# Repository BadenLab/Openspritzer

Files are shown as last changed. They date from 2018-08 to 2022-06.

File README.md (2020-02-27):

<p align="right">
<h1 align="center">Openspritzer</h1></p>
<h3 align="center">An open hardware pressure ejection system for reliably delivering picolitre volumes.</h3>
<p align="center"><h6 align="right">by C.J. Forman, H. Tomes, B. Mbobo, R.J. Burman, M. Jacobs, T Baden &
J.V. Raimondo</h6></p>
<p align="center"><h6 align="right">adapted by M.J.Y. Zimmermann</h6></p>
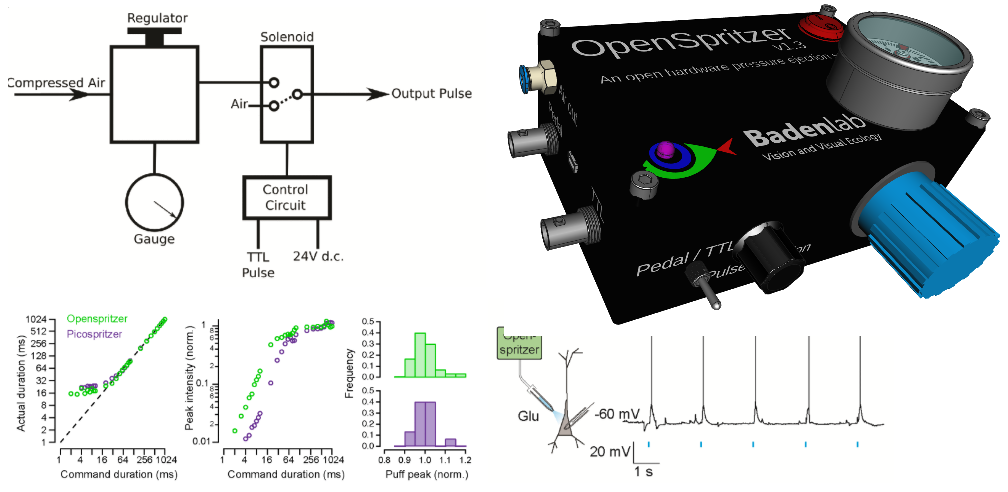
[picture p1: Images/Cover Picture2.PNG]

</p>

<p align="justify">Designed for ease of use, robustness and low-cost, the “Openspritzer” is an open hardware “Picospritzer” as routinely used
in biological labs around the world. The performance of Openspritzer and commercial alternatives is effectively indistiguishable.

<p align="justify">The system is based on a solenoid valve connected to a pressure gauge. Control can be attained directly via an external TTL pulse
or internally through an Arduino set by a rotary encoder. The basic setup can be put together for 3-400€, or substantially less if you
are prepare to shop around.

<p align="justify">We anticipate that due to its high performance and low cost Openspritzer will be of interest to a broad range of researchers working
in the life and physical sciences.</p>

This project is licensed under the [GNU General Public License v3.0](https://github.com/BadenLab/Openspritzer/blob/master/LICENSE)<br>
The hardware is licensed under the [CERN OHL v1.2](https://github.com/BadenLab/LED-Zappelin/blob/master/PCB/LICENSE)

***

- [A £350 DIY opensource microinjector](#Openspritzer,-a-DIY-opensource-microinjector.)
- [An efficient device that provides similar level of control as commercial systems](#Openspritzer-rivals-the-performance-of-commercial-systems.)
- [OpenSpritzer can deliver neurotransmitters with millisecond precision to control neural activity](#Openspritzer-in-neuroscience-experiments.)
- [OpenSpritzer is suitable for delivering infectious agents including viral delivery of opsins for optogenetics](#Openspritzer-for-microinjection-of-infectious-agents)

***

## Openspritzer, a DIY opensource microinjector.

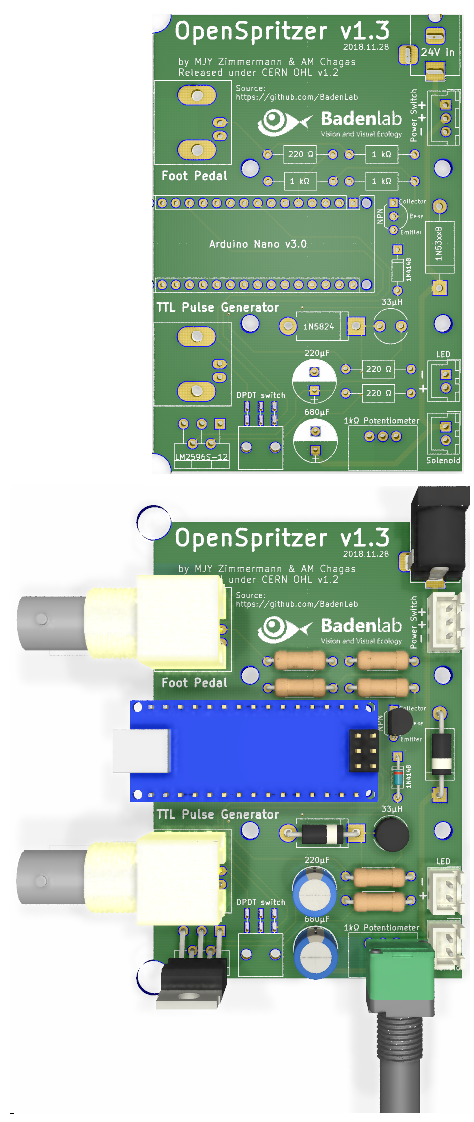
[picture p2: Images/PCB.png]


<p align="justify">Compared to similar commercial systems that can cost up to several thousand pounds, the cost of the fully equiped Openspritzer (~£350) makes it
particularly attractive for those wishing to pursue cutting-edge techniques in low ressource environments.</p>

This repository contains detailed [assembly instructions](https://github.com/BadenLab/Openspritzer/tree/master/Instruction%20Manual) and an operation manual for Openspritzer. The [bill of material](https://github.com/BadenLab/Openspritzer/blob/master/Bill%20of%20Materials/BOM.csv) details all pneumatic, mechanical and electronic components required along with possible supplier URL links.

To simplify the wiring assembly, we have designed a customed [circuit board](https://github.com/BadenLab/Openspritzer/tree/master/PCB). PCB prototype companies will only need the gerber.zip folder to be sent to them for production.

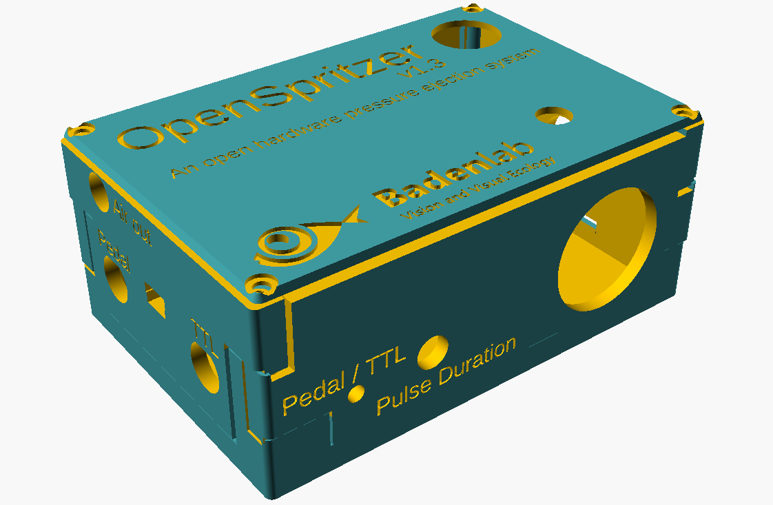
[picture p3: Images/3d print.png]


We used [OpenSCAD](http://openscad.org) to design [3D files](https://github.com/BadenLab/Openspritzer/tree/master/3D%20Designs) that could be printed to efficiently hold all openspritzer components.

The device is controled by an arduino nano. The [.ino code](https://github.com/BadenLab/Openspritzer/tree/master/Arduino%20Code) can be modified and uploaded as many times as you like. The way the Openspritzer code has been constructed allows simple modification of key parameters. These are all included at the beginning of the code for ease of reference.

***

## Openspritzer rivals the performance of commercial systems.

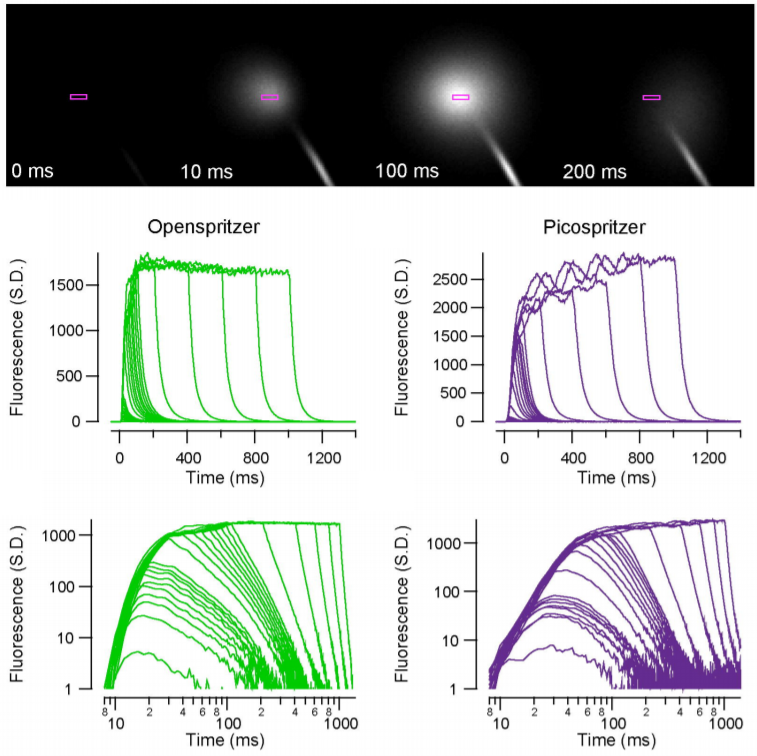
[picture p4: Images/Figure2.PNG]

Openspritzer control over dose delivery matches that of a leading commercial alternative.

<p align="justify">To directly assess the time precision and reliability of Openspritzer we visualised fluorescent dye puffs from a sharp microelectrode under two-photon microscopy. The images were taken from a puff with a duration of several seconds using a wide area scan (rectangles).

<p align="justify">Fluorescence profiles of different command-duration puffs are shown for Openspritzer (green) and Picospritzer, a popular microinjection system(purple), respectively. The same data is shown again in log-log space to highlight details of shorter pulses. Overall, both devices behave in a very similar way in terms of providing effective and near linear control over the total dosage.</p>

***

## Openspritzer in neuroscience experiments.

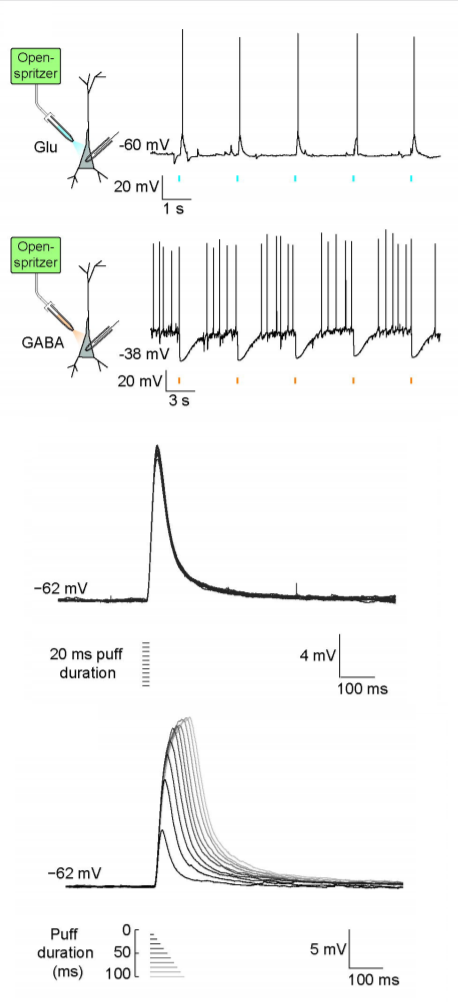
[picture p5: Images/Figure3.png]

Openspritzer controls neural activity by delivering neurotransmitters with millisecond precision.

<p align="justify">To demonstrate the utility of Openspritzer, we use it in a series of standard neurobiological applications:
We delivered precise amounts of glutamate(cyan) and GABA(orange) to hippocampal neurons to elicit time- and dose-precise excitatory and inhibitory responses respectively, while monitoring the voltage response of the recorded neuron in current-clamp mode.

<p align="justify">20 ms doses of glutamate (100 μM) reliably evoked excitatory postsynaptic potentials (EPSPs) and action potentials. Similarly, action potential activity elicited via somatic current injection could be suppressed by 20 ms puffs of GABA (100 μM).

<p align="justify">To assess the accuracy of the drug delivery, we applied 10 sweeps where a 20 ms glutamate puff was applied after 500 ms produced almost identical EPSPs demonstrating the precise timing of Openspritzer and highly conserved puff volumes.

<p align="justify">Then, to test the effect of command duration on effective dose delivey, we next applied puffs of increasing duration from 10 to 100 ms in 10 ms steps. Here, each additional 10 ms increase in duration produced a clear increase in both EPSP duration and amplitude. These results confirm the reliability and precision of Openspritzer for delivering small doses of an agent to a widely used biological sample in a controlled manner.</p>

***
***

<p align="justify">To demonstrate the utility of Openspritzer we performed multiple example experiments delivering agents ranging in size from single molecules to whole bacteria. Each experiment depended critically on the performance of the device. The spatio-temporal control of reagent delivery affored by Openspritzer is a primary feature of the device.

<p align="justify">Furthermore, with the emergence of a plethora of popular new techniques involving genetic manipulation of tissue and organisms, such as optogenetics and CRISPR, the demand for equipment with the functionality of Openspritzer is likely to increase.

<p align="justify">We anticipate that due to its high performance and low cost Openspritzer will be of interest to a broad range of researchers working in the life and physical sciences.</p>

<p align="center"><h6 align="right">Source: CJ. Forman et al, 2017 --  https://www.nature.com/articles/s41598-017-02301-2   </h6>

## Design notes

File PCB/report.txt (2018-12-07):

Plot file “C:\Users\Maxime\Documents\GitHub\Openspritzer\Printed Circuit Board\OpenSpritzer v1.2\gerber\OpenSpritzer_1.2-F.Cu.gbr” created.
Plot file “C:\Users\Maxime\Documents\GitHub\Openspritzer\Printed Circuit Board\OpenSpritzer v1.2\gerber\OpenSpritzer_1.2-B.Cu.gbr” created.
Plot file “C:\Users\Maxime\Documents\GitHub\Openspritzer\Printed Circuit Board\OpenSpritzer v1.2\gerber\OpenSpritzer_1.2-F.Adhes.gbr” created.
Plot file “C:\Users\Maxime\Documents\GitHub\Openspritzer\Printed Circuit Board\OpenSpritzer v1.2\gerber\OpenSpritzer_1.2-B.Adhes.gbr” created.
Plot file “C:\Users\Maxime\Documents\GitHub\Openspritzer\Printed Circuit Board\OpenSpritzer v1.2\gerber\OpenSpritzer_1.2-F.Paste.gbr” created.
Plot file “C:\Users\Maxime\Documents\GitHub\Openspritzer\Printed Circuit Board\OpenSpritzer v1.2\gerber\OpenSpritzer_1.2-B.Paste.gbr” created.
Plot file “C:\Users\Maxime\Documents\GitHub\Openspritzer\Printed Circuit Board\OpenSpritzer v1.2\gerber\OpenSpritzer_1.2-F.SilkS.gbr” created.
Plot file “C:\Users\Maxime\Documents\GitHub\Openspritzer\Printed Circuit Board\OpenSpritzer v1.2\gerber\OpenSpritzer_1.2-B.SilkS.gbr” created.
Plot file “C:\Users\Maxime\Documents\GitHub\Openspritzer\Printed Circuit Board\OpenSpritzer v1.2\gerber\OpenSpritzer_1.2-F.Mask.gbr” created.
Plot file “C:\Users\Maxime\Documents\GitHub\Openspritzer\Printed Circuit Board\OpenSpritzer v1.2\gerber\OpenSpritzer_1.2-B.Mask.gbr” created.
Plot file “C:\Users\Maxime\Documents\GitHub\Openspritzer\Printed Circuit Board\OpenSpritzer v1.2\gerber\OpenSpritzer_1.2-Dwgs.User.gbr” created.
Plot file “C:\Users\Maxime\Documents\GitHub\Openspritzer\Printed Circuit Board\OpenSpritzer v1.2\gerber\OpenSpritzer_1.2-Cmts.User.gbr” created.
Plot file “C:\Users\Maxime\Documents\GitHub\Openspritzer\Printed Circuit Board\OpenSpritzer v1.2\gerber\OpenSpritzer_1.2-Eco1.User.gbr” created.
Plot file “C:\Users\Maxime\Documents\GitHub\Openspritzer\Printed Circuit Board\OpenSpritzer v1.2\gerber\OpenSpritzer_1.2-Eco2.User.gbr” created.
Plot file “C:\Users\Maxime\Documents\GitHub\Openspritzer\Printed Circuit Board\OpenSpritzer v1.2\gerber\OpenSpritzer_1.2-Edge.Cuts.gbr” created.
Plot file “C:\Users\Maxime\Documents\GitHub\Openspritzer\Printed Circuit Board\OpenSpritzer v1.2\gerber\OpenSpritzer_1.2-Margin.gbr” created.
Plot file “C:\Users\Maxime\Documents\GitHub\Openspritzer\Printed Circuit Board\OpenSpritzer v1.2\gerber\OpenSpritzer_1.2-F.CrtYd.gbr” created.
Plot file “C:\Users\Maxime\Documents\GitHub\Openspritzer\Printed Circuit Board\OpenSpritzer v1.2\gerber\OpenSpritzer_1.2-B.CrtYd.gbr” created.
Plot file “C:\Users\Maxime\Documents\GitHub\Openspritzer\Printed Circuit Board\OpenSpritzer v1.2\gerber\OpenSpritzer_1.2-F.Fab.gbr” created.
Plot file “C:\Users\Maxime\Documents\GitHub\Openspritzer\Printed Circuit Board\OpenSpritzer v1.2\gerber\OpenSpritzer_1.2-B.Fab.gbr” created.
Plot file “C:\Users\Maxime\Documents\GitHub\Openspritzer\Printed Circuit Board\OpenSpritzer v1.2\gerber\OpenSpritzer_1.2-F.Cu.gbr” created.
Plot file “C:\Users\Maxime\Documents\GitHub\Openspritzer\Printed Circuit Board\OpenSpritzer v1.2\gerber\OpenSpritzer_1.2-B.Cu.gbr” created.
Plot file “C:\Users\Maxime\Documents\GitHub\Openspritzer\Printed Circuit Board\OpenSpritzer v1.2\gerber\OpenSpritzer_1.2-F.Adhes.gbr” created.
Plot file “C:\Users\Maxime\Documents\GitHub\Openspritzer\Printed Circuit Board\OpenSpritzer v1.2\gerber\OpenSpritzer_1.2-B.Adhes.gbr” created.
Plot file “C:\Users\Maxime\Documents\GitHub\Openspritzer\Printed Circuit Board\OpenSpritzer v1.2\gerber\OpenSpritzer_1.2-F.Paste.gbr” created.
Plot file “C:\Users\Maxime\Documents\GitHub\Openspritzer\Printed Circuit Board\OpenSpritzer v1.2\gerber\OpenSpritzer_1.2-B.Paste.gbr” created.
Plot file “C:\Users\Maxime\Documents\GitHub\Openspritzer\Printed Circuit Board\OpenSpritzer v1.2\gerber\OpenSpritzer_1.2-F.SilkS.gbr” created.
Plot file “C:\Users\Maxime\Documents\GitHub\Openspritzer\Printed Circuit Board\OpenSpritzer v1.2\gerber\OpenSpritzer_1.2-B.SilkS.gbr” created.
Plot file “C:\Users\Maxime\Documents\GitHub\Openspritzer\Printed Circuit Board\OpenSpritzer v1.2\gerber\OpenSpritzer_1.2-F.Mask.gbr” created.
Plot file “C:\Users\Maxime\Documents\GitHub\Openspritzer\Printed Circuit Board\OpenSpritzer v1.2\gerber\OpenSpritzer_1.2-B.Mask.gbr” created.
Plot file “C:\Users\Maxime\Documents\GitHub\Openspritzer\Printed Circuit Board\OpenSpritzer v1.2\gerber\OpenSpritzer_1.2-Dwgs.User.gbr” created.
Plot file “C:\Users\Maxime\Documents\GitHub\Openspritzer\Printed Circuit Board\OpenSpritzer v1.2\gerber\OpenSpritzer_1.2-Cmts.User.gbr” created.
Plot file “C:\Users\Maxime\Documents\GitHub\Openspritzer\Printed Circuit Board\OpenSpritzer v1.2\gerber\OpenSpritzer_1.2-Eco1.User.gbr” created.
Plot file “C:\Users\Maxime\Documents\GitHub\Openspritzer\Printed Circuit Board\OpenSpritzer v1.2\gerber\OpenSpritzer_1.2-Eco2.User.gbr” created.
Plot file “C:\Users\Maxime\Documents\GitHub\Openspritzer\Printed Circuit Board\OpenSpritzer v1.2\gerber\OpenSpritzer_1.2-Edge.Cuts.gbr” created.
Plot file “C:\Users\Maxime\Documents\GitHub\Openspritzer\Printed Circuit Board\OpenSpritzer v1.2\gerber\OpenSpritzer_1.2-Margin.gbr” created.
Plot file “C:\Users\Maxime\Documents\GitHub\Openspritzer\Printed Circuit Board\OpenSpritzer v1.2\gerber\OpenSpritzer_1.2-F.CrtYd.gbr” created.
Plot file “C:\Users\Maxime\Documents\GitHub\Openspritzer\Printed Circuit Board\OpenSpritzer v1.2\gerber\OpenSpritzer_1.2-B.CrtYd.gbr” created.
Plot file “C:\Users\Maxime\Documents\GitHub\Openspritzer\Printed Circuit Board\OpenSpritzer v1.2\gerber\OpenSpritzer_1.2-F.Fab.gbr” created.
Plot file “C:\Users\Maxime\Documents\GitHub\Openspritzer\Printed Circuit Board\OpenSpritzer v1.2\gerber\OpenSpritzer_1.2-B.Fab.gbr” created.

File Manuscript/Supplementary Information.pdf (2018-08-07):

## Supplementary Material

## Openspritzer: an open hardware pressure ejection system for reliably delivering picolitre volumes

Forman, C.J.¹,4§
, Tomes, H.

2

, Mbobo, B.²

, Baden, T¹,3,4§

., Raimondo, J.V.²,4§

Affiliations:
1) School of Life Sciences, University of Sussex, United Kingdom
2) Division of Physiology, Department of Human Biology, Neuroscience Institute and Institute of Infectious Disease and Molecular Medicine, Faculty of Health Sciences, University of Cape Town, Cape Town, South Africa
3) Institute for Ophthalmic Research, University of Tuebingen, Germany
4) TReND in Africa gUG (www.TReNDinAfrica.org)

§Correspondence: C.F.: chrisforman@cantab.net, T.B.: t.baden@sussex.ac.uk, J.V.R.: joseph.raimondo@uct.ac.za

Command duration is correlated to dosage

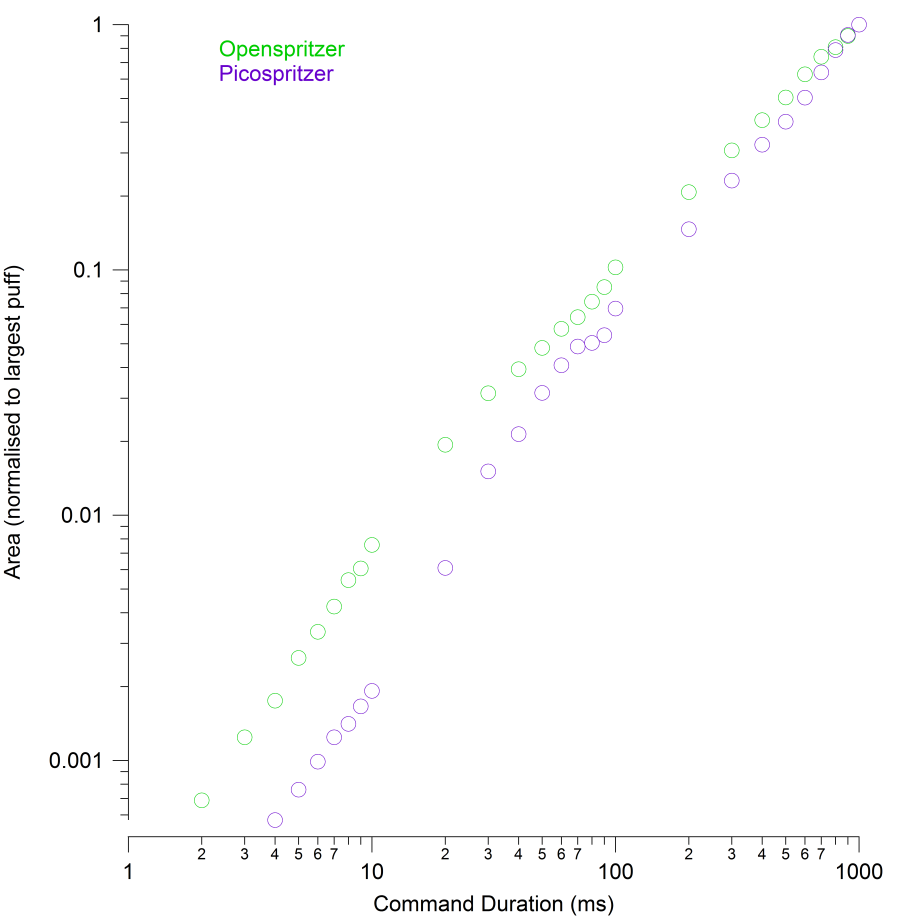
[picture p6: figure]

Supplementary Figure S1: The integrated area for each puff plotted against the command duration. The area under the puff profile is proportional to the dosage. Command duration and dosage are strongly correlated, regardless of the details of the puff profile over time.

Open Spritzer Construction

Overview

This document contains detailed assembly instructions and an operation manual for Openspritzer, and includes a parts list. The Arduino code and SCAD files for the exterior casing are provided and may be downloaded at http://raimondolab.com/Openspritzer/. The purpose of the device is to regulate the pressure and duration of a puff of compressed air. Typically the output port is connected to a glass puffer pipette which has been drawn into a sharp point with a narrow (<2-3 µm) diameter pore.
The device consists of a circuit board, a solenoid valve, a pressure regulator with a gauge and various interface components. Supplementary Fig. S2 shows the device without the covering lid and the solenoid displaced to expose the circuit board. The pressure regulator is mounted on the left and attached to the front panel via a retaining threaded ring that comes with the regulator. The circuit board is mounted onto attachment points on the floor of the box. It is situated next to the side wall containing the electronic interface components. There are two supports on which the solenoid can rest above the circuit board and an LED can be attached to a mount-point on the lid. There are also several retaining pillars which keep the solenoid in position. The lid has a block attached to it which acts to clamp the solenoid down when the box is closed.

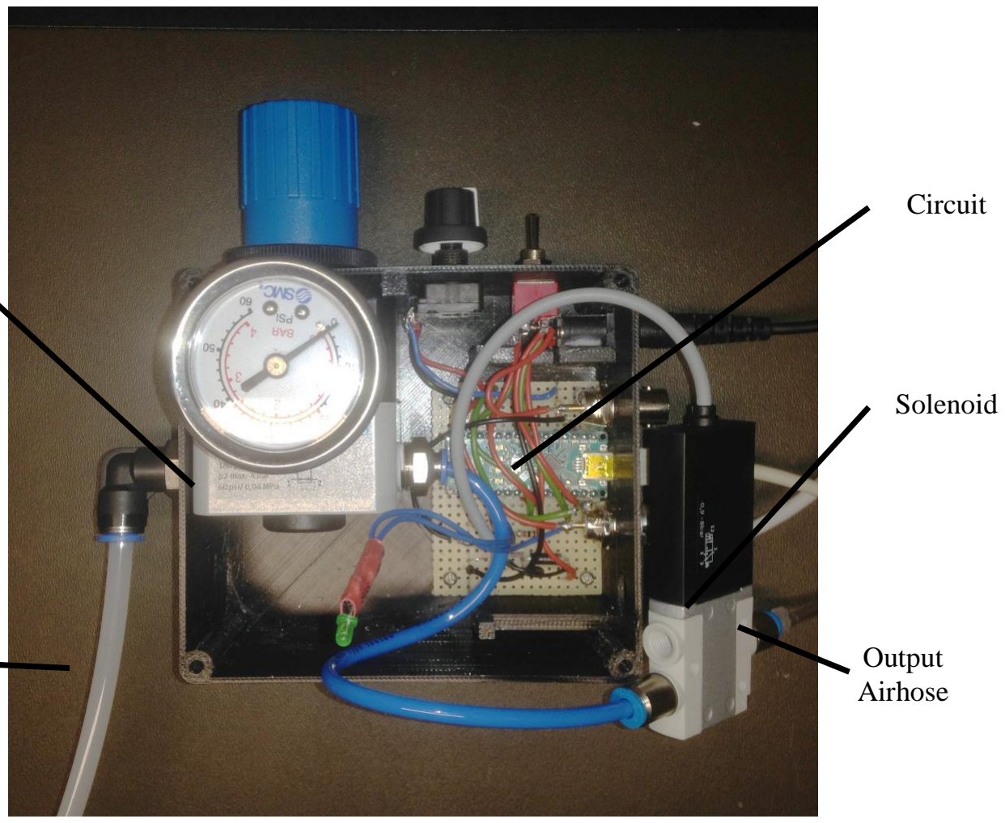
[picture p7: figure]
Solenoid; Circuit; Output Airhose

Supplementary Figure S2: Openspritzer consists of a pressure regulator, a solenoid and a control circuit. Its purpose is to control the strength and duration of a puff of compressed air, which is connected to a glass pipette that typically contains reagents for microinjection into biological samples.

Regulator
and Gauge

Input
Airhose

Parts List

Supplementary Table 1 has an exhaustive list of parts, suppliers and prices, allowing calculation of the total cost of parts, which is between £320 and £360 at submission, depending on how much of the full system one chooses to include. Much of the circuitry e.g. the Arduino, footswitch and toggle switch is purely for convenience. A core functional system consists of the regulator, solenoid and a much simpler control circuit under TTL pulse control. The simpler minimal circuit is indicated in the construction instructions below, and consists of the branch of the circuit containing the transistor.
In addition, prices are highly variable depending on local availability of components. For example the single most expensive component when we assembled ours was the regulator which cost £180 at the time. However, we subsequently found the same regulator for $43 in a different country. If one is prepared to shop around, we estimate that a functional Openspritzer without add-ons could be constructed for as little as £175. If one has all the components it takes approx 3 hours to construct a full Openspritzer depending on experience, and excluding the print time for the case and lid.
Frequently components only come in bags of 10 or 50 so if one only intends to fabricate a single device there may be an additional overhead of extra parts, depending on the flexibility of your supplier. For example ours cost £360 for the parts actually included in the device, but we paid £495 in total and now have some spare components for additional units.

4

Supporting Table S1 Parts schedule for Openspritzer

Part | Manufacturer | Manufacturers Number | Remarks | Quantity Essential

Component
Price

System
Price

Pack
| | | | | | | | price | Unit

Pneumatics
Solenoid (either 2 ms or 7 ms) | FESTO | MHE2-M1SH-3/2G-M7-K-RR | 2 ms response + cable | | 1 Yes | £80.00 | £80.00 | £80.00 | each
alternative | MHE2-M1H-3/2G-M7-K-RR | 7 ms response + cable
Precision pressure regulator | FESTO | LRP-1/4-4 | 0.05 to 4.0 bar | 1 Yes | £180.00 | £180.00 £180.00 each
Gauge | FESTO | MAP-40-4-1/8-EN | 0.0 to 4.0 bar, 1/8 inch thread
| alternative SMC | 4K84P | 0.0 to 4.0 bar, 1/8 inch thread | | 1 Yes | £30.00 | £30.00 | £30.00 | each
Push-in (6 mm) to thread (1/4") | FESTO | QSL-1/4-6 | 6 mm to 1/4 inch | | 1 Yes | £2.83 | £2.83 | £28.30 | Pack of ten
Push-in (4 mm) to thread (1/4") | FESTO | QS-1/4-4 | 4 mm to 1/4 inch | | 1 Yes | £1.76 | £1.76 | £17.60 | Pack of ten
Push-in (4 mm) to thread (M7) | FESTO | QSM-M7-4-I | 4 mm to M7 thread | | 2 Yes | £1.81 | £3.62 | £18.10 | Pack of ten
4mm OD plastic tubing | FESTO | PUN-4x0.75 | 4 mm OD and 10 bar | 12 cm | Yes | £0.09 | £0.09 | £35.50 | 50 m

Electronics
Arduino Nano | Arduino | | Arduino Nano | | 1 No | £4.00 | £4.00 | £4.00 | each
Darlington pair NPN transistor | Fairchild | KSP 13BU | Ic = 500 mA, Vces = 30 V | | 1 Yes | £0.12 | £0.12 | £1.20 | pack of ten
1 kΩ variable resistor | Vishay | 249BBHS0XB25102KA | panel mount | | 1 No | £7.53 | £7.53 | £7.53 | each
Knob for variable resistor | RS Online | 299-4957 | 6mm shaft radius | | 1 No | £0.17 | £0.17 | £0.85 | pack of five
DPDT switch | RS Online | 734-7016 | on-on panel mount | | 1 No | £1.13 | £1.13 | £5.65 | pack of five
SPST footswitch | RS Online | 335-319 | push-to-contact | | 1 No | £13.03 | £13.03 | £13.03 | each
24V dc desktop PSU 2.1 mm jack | RS Online | 436-058 | 24 V dc 1 A | | 1 Yes | £17.91 | £17.91 | £17.91 | each
2.1 mm right angle dc socket | RS Online | 884-0957 | 2.1 mm right angle | | 1 Yes | £0.93 | £0.93 | £4.65 | pack of five
Rect pin socket (through hole fem) | Digikey | SAM1222-01-ND | 1x1 | | 2 No | £0.81 | £1.62 | £1.62 | each
Rect pin socket (through hole fem) | Digikey | S7038-ND | 5x1 | | 1 No | £0.65 | £0.65 | £0.65 | each
Rect pin socket (through hole fem) | Digikey | 3M9514-ND | 3x1 | | 1 No | £0.64 | £0.64 | £0.64 | each
24 V Zener Diode | ON
Semiconductor 1N5359BG | 24 V | 1 Yes | £2.30 | £2.30 | £2.30 | each
1N4148 signal diode | Fairchild | 1n4148 | | | 1 No | £0.01 | £0.01 | £0.01 | each
3 mm LED | Digikey | 350-1557-ND | 3mm round, throughhole, grn | | 1 No | £0.95 | £0.95 | £0.95 | each

5

Mount for 3 mm LED | Digikey | 67-1330-ND | 3mm panel mount | | 1 No | £0.26 | £0.26 | £0.26 | each
220 Ω resistor | Digikey | CF14JT220RCT-ND | 220 Ω through hole resistor | | 3 No | £0.10 | £0.30 | £0.30 | each
1 kΩ resistor | Digikey | CF14JT1K00CT-ND | 1 kΩ through hole resistor | | 3 Yes | £0.10 | £0.30 | £0.30 | each
BNC connector male | RS Online | 423-1927 | 50 Ω Cable mount solder | | 1 No | £3.26 | £3.26 | £3.26 | each
BNC connectors female | Digikey | A97548-ND | Panel mount female | | 2 No | £1.60 | £3.20 | £3.20 | each
Matrix board | RS Online | 463-2819 | 2.5 mm pitch matrix board | | 1 Yes | £3.41 | £3.41 | £3.41 | each
Red, black, blue and green wire | RS Online | 331-862 | 20 AWG | 50cm | No | £0.19 | £0.19 | £11.29 | 30 m roll
Cable shrink | RS Online | 170-6377 | Shrunk diameter 1.2 mm. | 5cm | No | £0.04 | £0.04 | £1.02 | 1.2m

Mechanical
M3 x 24 screw | RS Online | 293-325 | M3 x 24 Hex socket cap | | 4 No | £0.27 | £1.06 | £13.29 | box/50
M3 nut | RS Online | 122-4400 | M3 nuts | | 4 No | £0.02 | £0.08 | £1.89 | bag/100
M2 x 5 machine screw | RS Online | 489-9264 | M2 x 5mm screw | | 4 No | £0.03 | £0.12 | £3.06 | bag/100
Super glue | RS Online | 330-4002 | Super glue bottle | | No | | | £4.05 | bottle
Totals | Cost
Only essential parts | £321.26
Full system | £361.50
Full System + Spares | £495.82

Construction

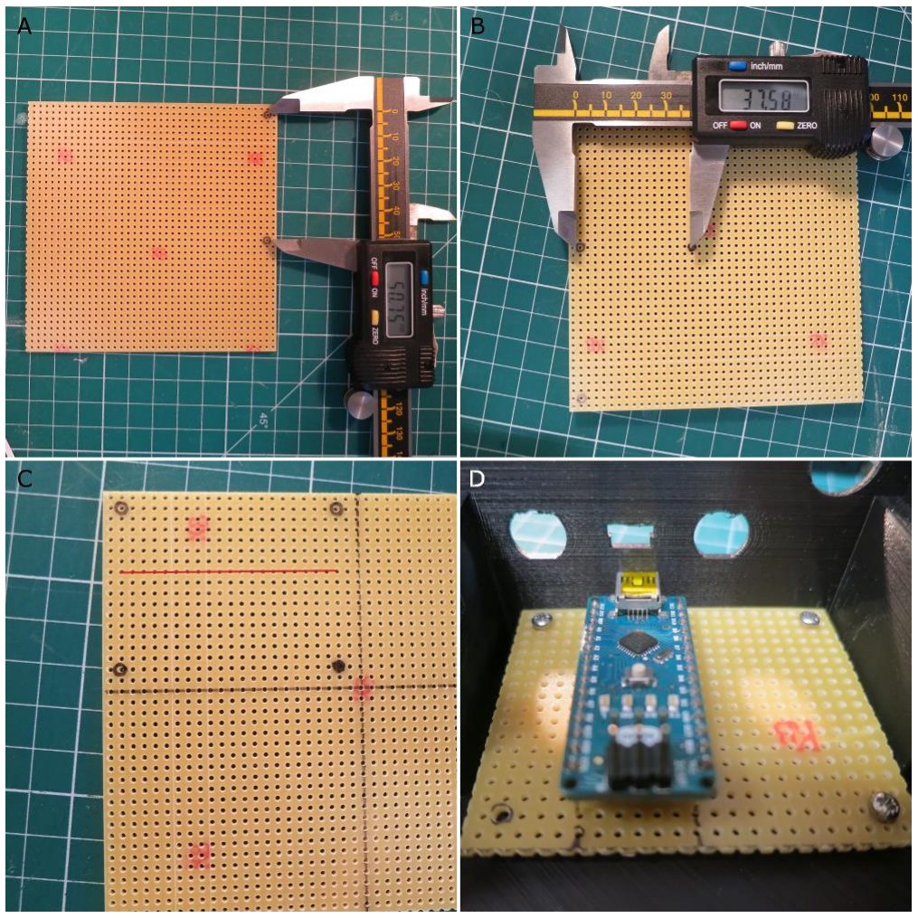
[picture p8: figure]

Supplementary Figure S3: A: Long edge of the matrix board measured between the mount point holes is 50.75 mm. B: The short edge is 37.6 mm. C: Ensure that the copper strips are parallel with the long edge and drill out the four mount point holes so they can comfortably contain an M2 screw without stressing the board. D: Test mount the board to correctly identify where to place the Arduino.

Matching the Circuit Board to the Box (Read BEFORE 3D printing the box!)

1. We used OpenSCAD (freely available at www.OpenSCAD.com) to design the box and lid respectively. The OpenSCAD script is provided. You may have to modify the measurements in the script to comply with the components that you have purchased.
2. In the SCAD file the box is aligned with the x-axis running parallel with the front and back panels of the box, and the y-axis parallel with the sides. The z-axis runs from bottom to top.
3. Prior to printing, ensure the mount points for the circuit board are spaced according to the holes on your matrix board (Fig. S3). In the OpenSCAD file you can adjust parameters MountPointWidth and MountPointLength to be the distance between the mounting holes in the board.

4. A pilot hole is incorporated down the centre of each mount point during printing and they are sufficiently tall to give clearance for any solder joints beneath the board. The mount points are thick enough to accommodate an M2 screw, although excessive torque can shear them off.
5. The overall dimension of the circuit board should be approx 60 by 40 mm, which includes the overhang beyond the mount points.
6. The copper strips of the circuit board should be parallel with the long axis of the board (y-axis of the device).
7. The overhang beyond the mount points is specified with the BoardEdgeX and BoardEdgeY parameters, which are used to control how far the mount points are from the nearest walls.
8. Once the mount points are the right distance apart, their overall group position along the Y-axis can be adjusted by changing the parameter BoardYPosition, which moves all four mount points together.
9. The positions of the two BNC holes on the side panel are defined relative to the opening for the USB port.
10. The position of the USB port can be adjusted using USBYOffset and USBZOffset. Changing these values will move the entire group of holes associated with the circuit board – except the power supply hole.
11. USBYOffset is the distance in mm along the y-axis from the center of the opening for the USB port to the center of the mountpoint nearest to the side wall and the front wall.
12. The position of the solenoid retainer pillar may also need adjustment prior to printing depending on which version of the solenoid was purchased, and whether it has the integrated or detachable cable.
13. The OpenSCAD file referred to here employs the solenoid variant which has the cable permanently attached rather than the variant that employs a plug.
14. If you have the variant with the plug then you will have to adjust the locations of the front retainer pillars to fit the solenoid in firmly. The x position of the retainer can be adjusted using SolRetOffsetX.
15. Widen the circuit board holes corresponding to the mount points with a 2 mm drill bit.
16. Test mount the circuit board to identify which holes in the matrix board the arduino must be soldered to.

Constructing the circuit board.

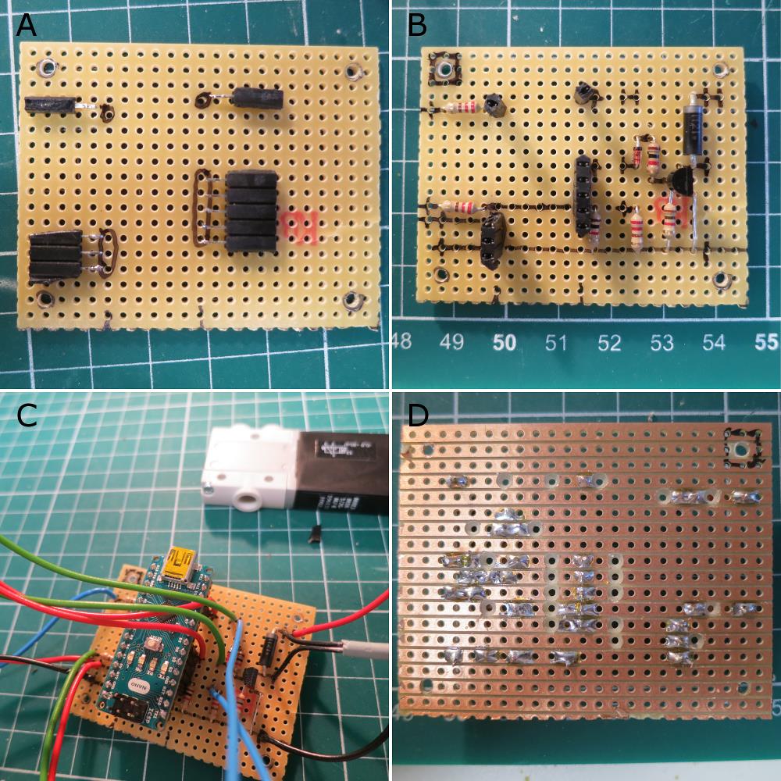
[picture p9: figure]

Supplementary Figure S4: A. Ensure the 5, 3, 1 and 1 terminal pin groups are in the correct place on the board. B. In the full circuit there are six resistors, two diodes and and a Darlington pair to solder into the correct positions. The marker pen indicates where connections exist under the board. C. Fly leads are attached wherever a short cross line is drawn on the circuit board. Ensure the solenoid cable is cut to an appropriate length before soldering (approx. 10 cm - see Fig. S2). D. Breaks in the copper strips beneath the board can be made using 2 mm drill bit rotated between finger and thumb.

1. Create four blocks of terminal strips containing 5, 3, 1 and 1 terminal pins, respectively.
2. Solder them in the positions indicated in Fig. S4A. It is important to get these in the right place so that Arduino matches up with the hole for the USB connector in the side panel.
3. The block of five sockets connects pins D5, D4, D3, D2 and GND to the board. The block of 3 connects 5V, BST and GND. The two single blocks connect D10 and A0. These are the only connections to the arduino that are needed.
4. Once the terminal blocks are in position all the components can be soldered to the board in the positions indicated in Fig. S4B. Note that if a stripped down circuit is being constructed (without the Arduino, LED or footswitch) then only the circuit downstream from the small signal diode needs to be constructed – the branch containing the Darlington pair. In this case the 5V signal control signal must be connected directly to the signal diode.
5. The connections that are to be maintained by the copper strips under the board are indicated with the marker pen above the board. Wherever a small vertical crossline is included there will be a fly lead attached to the board for connection to the panel mounted or external components.
6. Fig. S4D shows where the copper strips need to be removed beneath the board. This can be achieved easily by rolling a 2 mm drill bit between finger and thumb and manually drilling part of the way into the board through the copper strip. There is a square drawn around the same attachment hole in Figs 4B and 4D to aid interpretation. Not all these holes need to be drilled out but isolated connection points help to avoid stray capacitances between long unused copper strips, which may affect circuit behaviour.
7. Fig. 4C shows where wires need to be attached to the board. Here we used 18 AWG which only just fit through the holes. In practice 20 AWG will suffice. In general red wires are attached to 5V or 24V supplies, black wires to the GND, and the blue and green wires to various intermediate potentials.
8. When connecting the solenoid to the circuit it is worth coarse positioning the circuit board and the solenoid in position within the box to ensure that the cable is cut to an appropriate length.
9. Once the basic circuit has been laid out and soldered, it is useful to ensure that each isolated connection point is indeed isolated using a multimeter to verify the connections, and isolate any short circuits from stray solder etc, before installation.

Assembling the Box.

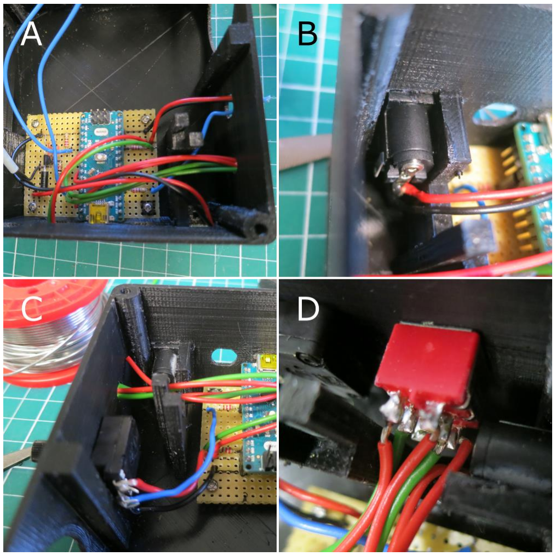
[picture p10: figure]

Supplementary Figure S5: A: The cable routes to their holes in the panel are shown, as well as a convenient method for determining a good length of cable. B: The power socket is superglued to the solenoid front support. C: Potentiometer wiring. D: DPDT wiring. The two lugs corresponding to the second ON state of the DPDT are wired together and the cable is routed to the BNC for the TTL pulse. Thus there are only five cables attached to the six pin DPDT. The sixth cable visible in image D is actually going to the 24 V powerline.

1. Screw the circuit board into position.
2. Cut each cable to an appropriate length. This can be achieved by routing the cables to the panel holes for which they are intended (as shown in Fig. S5A, and then cutting them on the other side of the panels. Leave the LED leads intact for the time being.
3. The cables for the 24 V power jack and the DPDT are routed through the gap in the front shelf underneath the solenoid.
4. The six upward facing pins on the Arduino should be cut off, desoldered or not installed in the first place as they interfere later with the pressure hoses and they are not used in this application. In the construction process during which the images were taken they were not removed until the point at which this mechanical problem was first encountered. However, it would be easier to remove them at this point.
5. Ensure that the Arduino is placed in position before soldering the panel components and mounting them on the panels.
6. Mount the 24 V power socket before any of the other panel components (see Fig. S5B). Ensure that the socket can fit squarely into the opening before soldering it. You may need to adjust the size of the hole with a craft knife or a rasp. If you acquired the power socket in the parts list then there is a small plastic pin underneath the power socket which fits into the hole in the small panel beneath the power socket opening. Once you can install and remove the power socket easily then solder the cables into place ensuring the correct polarity. The central core of the socket should be positive. Then apply a small blob of superglue to the side of the power socket to hold it in place against the solenoid front shelf which is positioned perfectly square with the opening.
7. Next mount the potentiometer, by soldering the leads as shown in Fig. S5C and inserting the spindle through the panel hole, keeping the solder tags to the left hand side, by the regulator pillar. The potentiometer is held in place with a locking nut on the outside of the device. Cut the spindle to length with a hack saw and then attach a knob, as desired.
8. Fig. S5D shows the DPDT in place. To correctly connect this switch strip a single red cable to reveal about 1 cm of bare wire. The wire can be inserted simultaneously through the two lugs that belong to different sides of the DPDT but relate to the same switch state, thus shorting the two sides of the DPDT for that input. Solder the wire in place to both lugs. The other end of this wire will go to the BNC connector for an external TTL pulse, and will drive both the LED and transistor circuit simultaneously.
9. Next solder the green wires from the LED and transistor branches of the circuit to the pole of the DPDT on the two central lugs. The top two red wires for the other DPDT switch state are routed from the D10 and D5 Pins respectively. To match the code in the repository as it was at publication then make sure to connect these to their correct respective green wires so that pin 10 controls the LED and pin 5 controls the solenoid.
10. Once all six wires are in place the DPDT can be mounted on the panel, which requires use of the gap in the front solenoid shelf to install the switch. The orientation of the DPDT is set by a locking washer which has a small lug on it. Drill a small hole part way into the front wall panel at the appropriate distance directly below the hole for the switch. The lug on the locking washer sits into the hole and locks the orientation of the switch into a vertical plane. The locking nuts can then be screwed into place to hold it tight. The locking washer could be placed on the inside or the outside of the panel. Take care not to over-tighten the locking nuts as this risks shearing the collar on the switch.

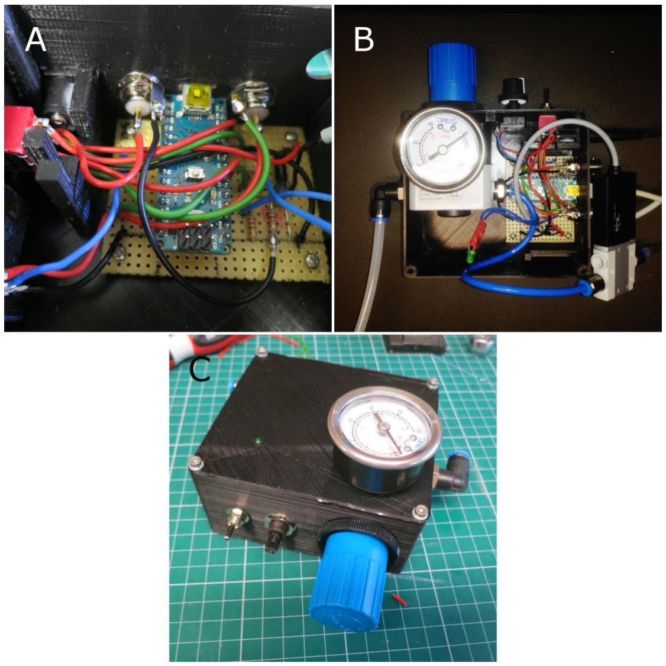
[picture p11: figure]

Supplementary Figure S6: A: The core pin of the TTL BNC is connected to the second ON position of the DPDT and the ground tag to the ground of the circuit. The core pin of the footswitch BNC is connected to 5 V and the ground tag is connected via a resistor to Pin D2 for monitoring. There is also a pull down resistor in the circuit to ensure an off reading when the switch is not closed. B: A workable arrangement of hoses, solenoid cable and LED wires. The hose connects port 2 of the regulator to port 1 on the solenoid, and the LED is the final component to be soldered into place. C: The final addition is the gauge which screws directly into the regulator through the lid.

11. The next step is to install the BNC connector for the external TTL pulse. The connectors are easily placed into the hole and, locked in place with a locking nut. Care must be taken to include the solder tag for grounding the BNC. The shorted lugs on the DPDT should be connected to the central pin of the BNC and the grounding tag should be connected to the ground on the circuit board. This can be achieved by soldering it directly to the end of the resistor as shown in Fig. S6A. Or you could install this wire earlier, along with all the others, from any spare hole on the ground line.
12. The second BNC is for the foot switch. The 5 V line should be connected to the central pin and the grounding tag should be connected to the green wire shown, which connects via a resistor to pin D2 which monitors the foot switch.
13. Fig. S6B indicates how to install the regulator and solenoid. First the locking ring is removed from the regulator and the knob is fed through the large circular aperture ensuring that port 1 is facing to the left panel and the gauge hole is exposed on the top surface. Although it is shown in the image, do not attach the gauge at this time.
14. A 1/4 inch thread to 4 mm push fit adaptor is placed in port 2 of the regulator to which a 10 cm blue hose is then attached.
15. The hose is routed above the circuit board and back out to the rest of the box, ensuring that it passes around the back of the solenoid cable. The solenoid can then be placed into position ensuring that port two is next to the output hole in the panel.
16. The LED wires should come up inside the solenoid cable. Place heat shrink tubing on to the LED leads before soldering the LED, ensuring the correct polarity of the LED.
17. After the LED is soldered in place, cover the contacts with the heat shrinking tubing and use a heat gun or soldering iron to shrink the tubing.
18. The blue hose can then be inserted into port 1 of the solenoid.
19. Remove the blocking screw from the top of the regulator unblocking the aperture for the gauge.
20. An L-shaped adaptor is inserted into port 1 of the regulator through the left hand side panel.
21. An M7-threaded to 4mm push fit adaptor is insert into port 2 of the solenoid through the right hand side panel.
22. The lid is then placed coarsely in position, and the LED mount is placed in the hole. The LED is placed in turn into the mount, which should lock it in place.
23. If you purchased the SMC gauge then use a hack saw to remove the two side screws from the gauge. Don’t remove the central brass screw that is the pressure input to the gauge.
24. You can then place the gauge though the lid and screw it into the regulator.
25. To screw the lid into place you must first insert a hex-nut into the holes on the base of the box. You can do this by part screwing the nut onto a second screw and pushing it up inside, and then unscrew the screw.
26. Once the nut is in the hole (even partially) you can draw it up inside from above with the screws that hold the lid in place.

Programming the Arduino on board Openspritzer

1. Once Openspritzer is assembled the Arduino must be programmed.
2. Download and install Arduino programming environment on your computer (www.Arduino.org).
3. Open the .ino code for Openspritzer which is included in the Supplementary Materials.
4. Compile and upload code to the Openspritzer by connecting the USB port of Openspritzer to the USB port of your computer and clicking on the "Upload" icon in the top left corner of the screen.
5. Code can be modified and uploaded as many times as you like. The way the Openspritzer code has been constructed allows simple modification of key parameters such as the base unit of time. These are all included at the beginning of the code for ease of reference and are listed in supporting table 2.
6. IMPORTANT: The first time that the Arduino is used the POT_VALUE_LOW and POT_VALUE_HIGH parameters should be measured. A Serial.println statement is included in the code to allow monitoring of this value over the serial port.
7. To measure these values open the serial port monitoring window in the Arduino programming environment and then sweep the potentiometer from low to high.
8. The two parameters POT_VALUE_HIGH and POT_VALUE_LOW should be initialised to the highest values and lowest values observed in the monitoring window output.
9. This is used in the calculations of the pulse duration and will vary from Openspritzer to Openspritzer depending on the precise value of the resistances used in the construction of the device.

Operating Openspritzer

1. Connect an air compressor to the input port 1 of the regulator via the L-shaped adaptor.
2. The output airhose must be connected to the application.
3. Connect the 24 V power supply to operate the solenoid.
4. It is not necessary to use the arduino to operate the solenoid if you have a convenient method for producing 5 V TTL pulses, such as PulseQ electrophysiology package (Funetics) running on Igor Pro (Wavemetrics) in conjunction with the ITC 1600.
5. To use TTL pulses ensure the DPDT switch is in the TTL position. Whenever the 5 V line is high the solenoid will open and release compressed air from the output valve.
6. A good pressure for sharp crisp pulses, which helps the solenoid to close again, is 1.4 bar (20 psi). Important: When first connecting high-pressure air to Openspritzer, e.g. from a compressor or air-tank, make sure that the Openspritzer gauge is near zero. A too-high line pressure (>>1.4 bar) risks irreversibly damaging the solenoid.
7. For convenience in darkened circumstances the LED will also illuminate whenever the 5 V line is high.
8. Using the Arduino to drive the puffer allows operation with the external footswitch.
9. To operate with a footswitch the DPDT must be placed in Arduino mode and a 5 V power supply provided to the Arduino via the USB port.

10.The 5 V power supply can be any standard USB power supply and need not be a computer.

11.Attaching a computer at operation time allows for dynamic reprogramming of the Arduino during experimentation, which can be very useful. E.g. resetting the base time unit.

12.When the Arduino is first powered on the Openspritzer enters the potentiometer monitoring loop to intialise the pulse duration. During this process The LED lights up for half a second and then blinks to indicate the pulse duration. Such behaviour also indicates that the code is running properly.

13.To operate the unit press the foot-button and after 400 milliseconds a puff of a predefined duration will occur.

14.The LED will illuminate during the puff to give visual confirmation that the puff has occurred.

15.The duration of the puff can be changed by adjusting the potentiometer, which selects the integer number of times that the base time unit is repeated during the puff.

16.When the potentiometer is changed Openspritzer goes into a monitoring mode during which time the LED is continuously lit.

17.When the potentiometer stops changing Openspritzer blinks the LED to indicate the new time duration.

18.For example: if seven blinks occur after leaving the monitoring mode and the base time unit is set to 10 ms in the software then the duration of the pulse will be 7 x 10 ms = 70 ms.

19.If the button is clicked twice within the first four hundred milliseconds after the first click then a pre-programmed sequence of puffs will occur.

20.The default sequence is 28 pulses ranging from 2 ms up to 1000 ms and spaced two seconds apart. This is the method used to generate the puff sequences used in figure 2 of the main paper.

21.The pulse sequence can be interrupted by clicking the foot button during the sequence upon which occurrence the led will blink rapidly and then revert to stand-by.

Openspritzer Code Parameters

Keyword | Default Setting | Meaning
TIMEUNIT | 100 | Base time unit in milliseconds.
POT_VALUE_LOW | 0 | Analogread of lowest setting of potentiometer (measured).
POT_VALUE_HIGH | 1023 | Analogread of highest setting of potentiometer (measured).
SENSITIVITY | 10 | Number of settings of potentiometer.
POT_NOISE | 5 | Range of fluctuations in the pot_value when static.
STABILITY_TIME | 500 | Number of milliseconds stability required to accept a new pot_value.
MONITOR_DELAY | 100 | Delay between loops of the analog monitoring mode.
PAUSE_BEFORE_BLINK | 500 | Milliseconds delay before blinks occur after exiting analog monitoring mode.
BLINK_ON_DURATION | 100 | Duration for which the LED is on during the blinking phase.
BLINK_OFF_DURATION | 250 | Duration between blinks in the blink phase.
NUM_PROGRAMMED_PULSES | 19 | Number of puffs in hard coded sequence.
PROGRAMMED_SEQUENCE[19] | d
1
| ,d
| 2 ,...,d
n
| | Puff duration sequence in ms.
PROGRAMMED_PULSE_DELAY | 2000 | Delay between puffs in programmed sequence.
MONITOR_FOOTSWITCH_PERIOD | 400 | Period to monitor for second button click.
FOOTBUTTONDELAY | 1000 | Main loop time delay allows button release.

Supplementary Table S2: Main user adjustable parameters of Openspritzer software

1. Supplementary Table S2 indicates the main parameters in the code which can be adjusted by the user and uploaded to Openspritzer to allow customised behaviour.
2. The user is free to write any code they wish to monitor the foot button, read the potentiometer, blink the LED or operate the solenoid. This code included alongside this paper was found to be convenient when used to record the data in the paper.
3. The monitoring algorithm relies on the POT_NOISE parameter to decide whether or not the potentiometer has settled.
4. To set POT_NOISE, monitor the serial port output during the analog monitoring procedure and find the POT_VALUE measured by the analogread command. POT_NOISE should be larger than any fluctuations in the pot_value when it is not being altered.
5. During testing, depending on which power supply was used, it was found that a reasonable value for POT_NOISE was 5.
6. The SENSITIVITY parameter increases the number of settings that are available by adjusting the potentiometer, which could be used to yield higher precision in the duration, or increase the overall range of durations.
7. If SENSITIVITY is set too high then the range of potentiometer values assigned to each setting will become smaller than POT_NOISE and the monitoring algorithm will never exit.
8. For example, typically there are 1024 values available for the pot_value, so a SENSIVITY of 10 will give 113 different values that correspond to each setting.
9. The lowest position of the potentiometer is defined to give yield a multiplier setting of 1 and the highest setting yields SENSITIVITY.

10.Depending on the linearity of the potentiometer the other values will be dispersed evenly.

11.A reasonable size range of pot_values should be assigned to each integer setting to give the user a chance to find that value.

12.In practice a SENSITIVITY of 10 settings was found to be adequate and easy to gauge the right rotation of the potentiometer.

13.The probability of mis-counting the confirmation pulses become much higher over ten pulses.

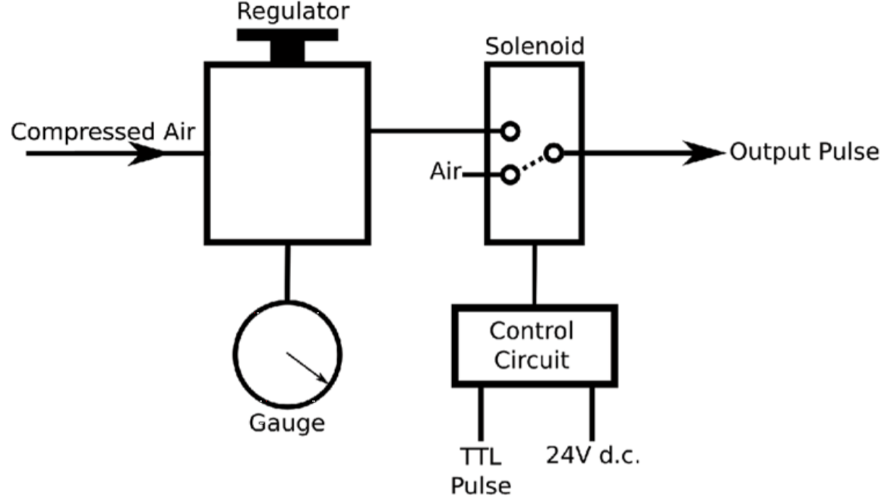
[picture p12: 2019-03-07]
Images/schematics.PNG

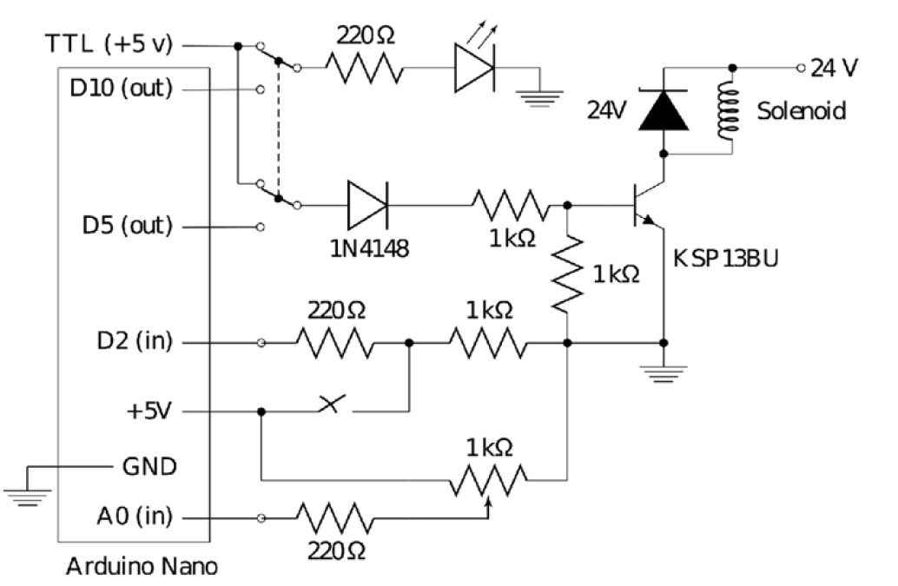
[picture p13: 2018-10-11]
Images/Electric Circuit.png

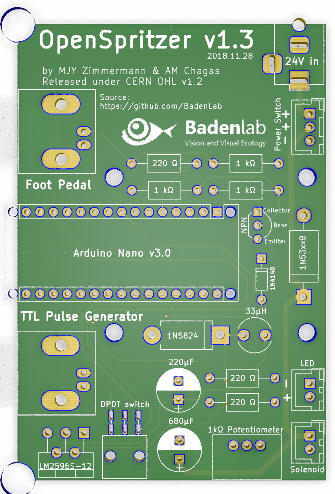
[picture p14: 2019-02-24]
Images/PCB Board.png

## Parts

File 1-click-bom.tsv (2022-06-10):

References | Qty | Description | Manufacturer | MPN | Manufacturer | MPN | Manufacturer | MPN | Manufacturer | MPN | Digikey | Mouser | RS | Newark | Farnell
A1 | 2 | 2.54 mm header 15 pin 1 row | Samtec inc | SSA-115-S-T |  | SSW-115-01-T-S | Samtec | SSA-115-S-T | Samtec | SSW-115-01-T-S | SAM1213-15-ND | 200SSW11501TS | 1981501 |  | 2779587
C1 | 1 | 680 uf electrolict cap | Rubycon | 35ZLH680MEFC10X23 |  |  |  |  |  |  | 1189-1749-ND | 23235ZLH680MEFC10X2 | 7037560 |  | 8126771
C2 | 1 | 220 uf electrolitic cap | Panasonic | EEUFC1V221 | Panasonic | EEU-FC1V221 |  |  |  |  | P10297-ND | 667EEUFC1V221 | 3150726 |  | 9692282
D1 | 1 | Red LED 5mm | kingbright | L-53HD | Kingbright | L-53HD | Vishay | VLCS5830 |  |  | 754-2157-ND | 78VLCS5830 | 2285988 |  | 2889660
D2 | 1 | Switching Diode, 400mA 100V | On Semiconductor | 1N4148TR | Vishay | 1N4148TR | ON Semiconductor | 1N4148TR |  |  | 1N4148FSCT-ND | 5121N4148TR | 6715477 |  | 9843680
D3 | 1 | 24V Zener Diode 5% 5 W | On Semiconductor | 1N5359BG | ON Semiconductor | 1N5359BG |  |  |  |  | 1N5359BGOS-ND | 8631N5359BG | 463808 |  | 9558179
D4 | 1 | 40V 3A, Schottky Diode | STM | 1N5822RL | STMicroelectronics | 1N5822RL |  |  |  |  | 497-14742-1-ND | 5111N5822TR | 7146819 |  | 3214544
J1,J4 | 2 | Right Angle 50Ω PCB Mount Bulkhead Fitting BNC Connector, | TE connectivity | 1-1337542-0 | TE Connectivity | 1-1337542-0 |  |  |  |  | A97552-ND | 571113375420 | 5121203 |  | 1020954
J2 | 1 | Barrel jack | Cliff | FC68148 DC10A | RS pro | 1438915 |  |  |  |  |  |  | 1438915
J3;D1 | 2 | JST Header 2 pin B2B XH series | JST | B2B-XH-A(LF)(SN) |  |  |  |  |  |  | 455-2247-ND |  | 8201554 |  | 1516276
L1 | 1 | 33 μH ±10% Ferrite Radial Inductor | Bourns | RLB0914-330KL |  |  |  |  |  |  | RLB0914-330KL-ND | 652RLB0914330KL | 8118853 |  | 2309242
Q1 | 1 | NPN darlington | Fairchild | KSP 13BU | ON Semiconductor | KSP13BU |  |  |  |  | KSP13BU-ND | 512KSP13BU | 7390344 |  | 2825113
R1, R2, R3 | 3 | 220 resistor 250mW | Stackpole electronics | CF14JT220R | Stackpole Electronics | CF14JT220R | RS-PRO | 707-8176 |  |  | CF14JT220RCT-ND |  | 707-8176
R4, R5, R6 | 3 | 1k resistor 250mW | Yageo | SQP500JB-1K | TE Connectivity | CFR16J1K0 |  |  |  |  | 1.0KW-5-ND | 603SQP500JB1K | 1251150 |  | 2329486
RV1 | 1 | 1k 1W 10% potentiometer | Vishay | 249FGJS0XB25102KA | Bourns | 51CAD-E28-A10L |  |  |  |  | 51CAD-E28-A10L-ND | 65251CADE28A10L | 410176 |  | 1107271
SW1 | 1 | DPDT | Multicomp | 2MD3T2B2M6RE | RS-PRO | 734-7205 |  |  |  |  |  |  | 734-7205 |  | 1550091
SW2 | 1 | JST Header 3 pin B3B XH series | JST | B3B-XH-A(LF)(SN) |  |  |  |  |  |  | 455-2248-ND |  | 8201557 |  | 1516277
U1 | 1 | step down voltage regulator | Texas instruments | LM2596T-12/NOPB | Texas Instruments | LM2596T-12/NOPB |  |  |  |  | LM2596T-12/NOPB-ND | 926LM2596T12/NOPB | 5333721 |  | 1693993
A1 | 1 | Arduino Nano | Arduino | A000005 |  |  |  |  |  |  |  |  | 696-1667

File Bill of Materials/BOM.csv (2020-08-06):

reference | Name | Manufacturer | Order ID | Retailer | Quantity | Observation 1 | Observation 2
 | Solenoid (either 2 ms or 7 ms model) | FESTO | MHE2-M1SH-3/2G-M7-K-RR | Kiowa | 1 | Pneumatics | 2 ms response + cable
 | Precision pressure regulator | FESTO | LRP-1/4-4 | RS | 1 | Pneumatics | 0.05 to 4.0 bar
 | Gauge | FESTO | MAP-40-4-1/8-EN | Kiowa | 1 | Pneumatics | 0.0 to 4.0 bar, 1/8 inch thread
 | Push-in (6 mm) to thread (1/4") | FESTO | QSL-1/4-6 | RS | 1 | Pneumatics | 6 mm to 1/4 inch
 | Push-in (4 mm) to thread (1/4") | FESTO | QS-1/4-4 | RS | 1 | Pneumatics | 4 mm to 1/4 inch
 | Push-in (4 mm) to thread (M7) | FESTO | QSM-M7-4-I | RS | 2 | Pneumatics | 4 mm to M7 thread
 | 4mm OD plastic tubing | FESTO | PUN-4x0.75 | RS | 12 cm | Pneumatics | 4 mm OD and 10 bar
 | PicoNozzle Kit | World Precision Instrument | 5430 - x | WPI | 1 | Pneumatics | for 1.0 / 1.2 / 1.5 / 2.0 mm glass pipettes
A1 | Arduino Nano | Arduino |  | RS | 1 | Electronics | nano
A1 | PCB socket | Samtec | SSW-116-02-G-S | RS | 2 | Electronics | 1 row, 15 pin
 | Darlington pair NPN transistor | Fairchild | KSP 13BU | Farnell | 1 | Electronics | Ic = 500 mA, Vces = 30 V
RV1 | 1 k ohm variable resistor | Vishay | 249FGJSPXB25102KA� | RS | 1 | Electronics | panel mount
 | Knob for variable resistor | RS Online | 783-0192 | TE Connectivity | 1 | Electronics | 6.35mm shaft radius
SW1 | DPDT switch | Multicomp | 2MD3T2B2M6RE | Farnell | 1 | Electronics | ON-(OFF)-ON panel mount
 | SPST footswitch | RS Online | 335-319 | RS | 1 | Electronics | push-to-contact
 | 24V DC desktop PSU 2.1 mm jack | RS Online | 436-058 | RS | 1 | Electronics | 24 V dc 1 A
 | 2.1 mm right angle DC socket | RS Online | 884-0957 | RS | 1 | Electronics | 2.1 mm right angle
D3 | 24 V Zener Diode | Semiconductor | 1N5359BG | Farnell | 1 | Electronics | 24V
D2 | 1N4148 signal diode | Fairchild | 1n4148 | Farnell | 1 | Electronics | 24V
R4;R5;R6 | 1 k ohm resistor | Digikey | CF14JT1K00CT-ND | Digikey | 3 | Electronics | 1 k? through hole resistor
R1;R2;R3 | 220 ohm resistor | Stackpole electronics | CF14JT220R | Digikey | 3 | Electronics | 220 ? through hole resistor
 | Voltage step-down regulator | RS Online | 533-3743 | RS | 1 | Electronics | 5V, 3A
C1 | Capacitor 680 uF | RS Online | 526-1569 | RS | 1 | Electronics | 24V minimum
C2 | Capacitor 220 uF | RS Online | 526-1480 | RS | 1 | Electronics | 24V minimum
D4 | Diode 1N5824 | RS Online | 714-6819� | RS | 1 | Electronics | 24V minimum
L1 | Inductor 33 uH | Bourns | RLB0914-330KL | Farnell | 1 | Electronics
 | 3 mm LED | Digikey | 350-1557-ND | Digikey | 1 | Electronics | 3mm round, throughhole, grn
 | Mount for 3 mm LED | Digikey | 67-1330-ND | Digikey | 1 | Electronics | 3mm panel mount
J1;J4 | BNC coaxial connectors | TE Connectivity | 1-1337542-0 | Farnell | 2 | Electronics | Right angle jacks, 50ohm
 | Cable Mount BNC Connector | RS Online | 546-3721 | RS | 1 | Electronics | Plug Crimp Termination
J3,D1 | 2 way JST Female Connector Housing | RS Online | 820-1611 | JST | 2 | Electronics
SW2 | 3 way JST Female Connector Housing | RS Online | 820-1614 | JST | 1 | Electronics
 | 2 way JST PCB header | RS Online | 820-1554 | JST | 2 | Electronics
SW2 | 3 way JST PCB header | RS Online | 820-1557 | JST | 1 | Electronics
 | 2 distinc colour wires | RS Online | 331-862 | RS | 20 cm | Electronics | 20 AWG
 | Shrink tube | RS Online | 170-6377 | RS | 5 cm | Electronics | Shrunk diameter 1.2 mm
 | Rocker LED switch |  |  | Ebay | 1 | Electronics | Round Switch / 3 pins
 | M3 x 10mm screw | RS Online | 660-4636 | RS | 4 | Mechanical | M3 x 10 Hex socket cap
 | M3 nut | RS Online | 122-4400 | RS | 4 | Mechanical | M3 nuts
 | M4 x 50mm Hex Socket Cap Screws | RS Online | 304-4592 | RS | 4 | Mechanical | M4 x 50
 | M4 nut | RS Online | 189-579 | RS | 4 | Mechanical | M4 nuts

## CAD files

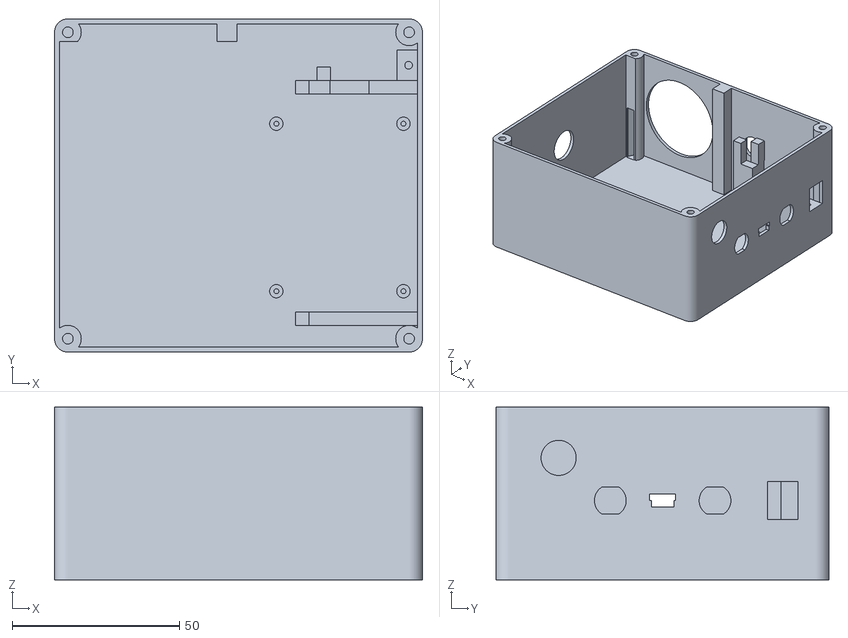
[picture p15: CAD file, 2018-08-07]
3D Designs/v0.1 - DIY Board/Puffer Body.stl
110.0 x 99.6 x 51.6

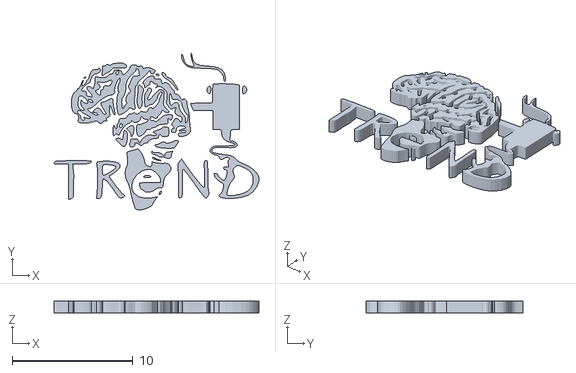
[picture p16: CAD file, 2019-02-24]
3D Designs/v1.3 - Customed PCB/Logo/Trend.stl
17.0 x 13.0 x 1.00

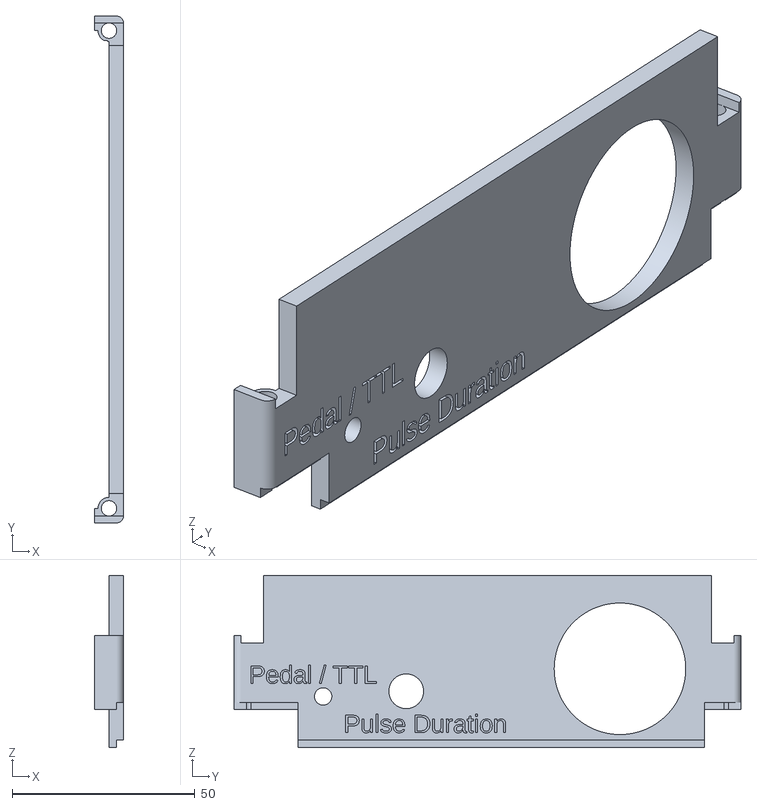
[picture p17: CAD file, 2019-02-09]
3D Designs/v1.3 - Customed PCB/STL Files/OpenSpritzer_Front.stl
8.00 x 138.8 x 47.1

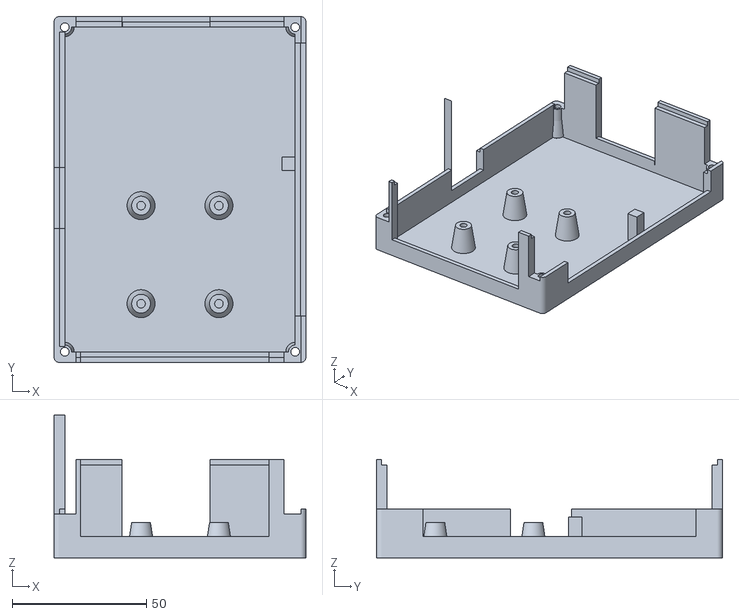
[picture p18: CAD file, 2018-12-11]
3D Printing Files/v1.3 - Customed PCB/Bottom.stl
93.8 x 128.8 x 53.1

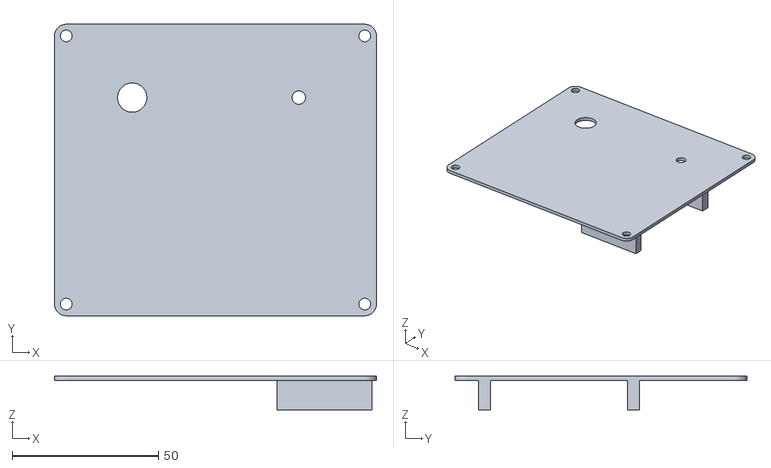
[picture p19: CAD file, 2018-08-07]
3D Designs/v0.1 - DIY Board/Puffer Lid.stl
110.0 x 99.6 x 11.6

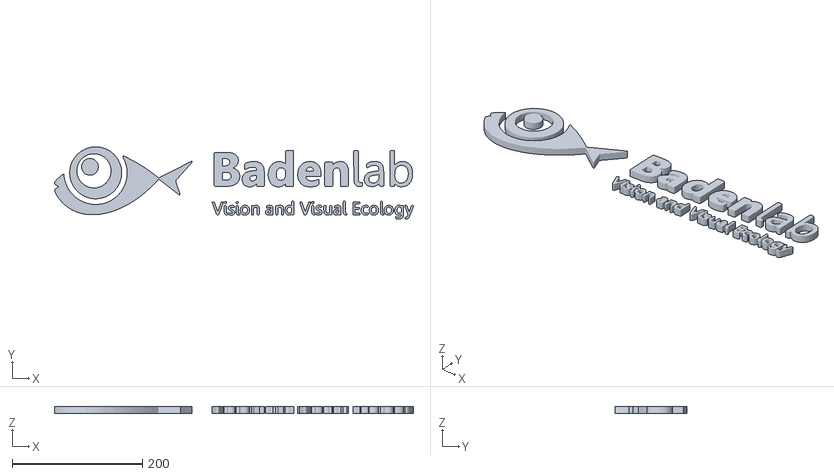
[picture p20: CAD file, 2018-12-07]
3D Designs/v1.3 - Customed PCB/Logo/Badenlab_logo.stl
550.3 x 111.0 x 10.0

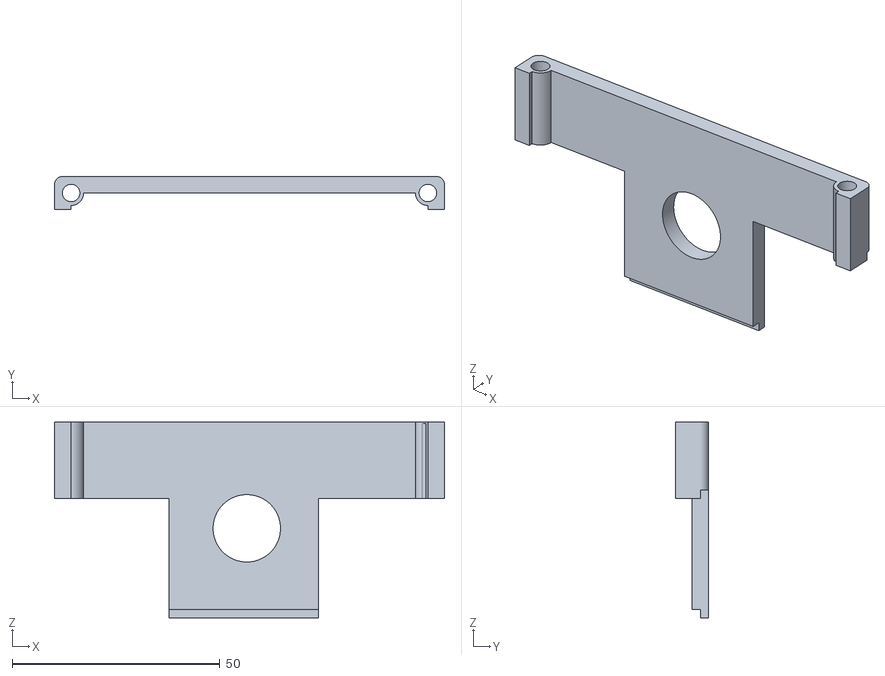
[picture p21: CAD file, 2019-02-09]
3D Designs/v1.3 - Customed PCB/STL Files/OpenSpritzer_Right.stl
93.8 x 8.00 x 47.1

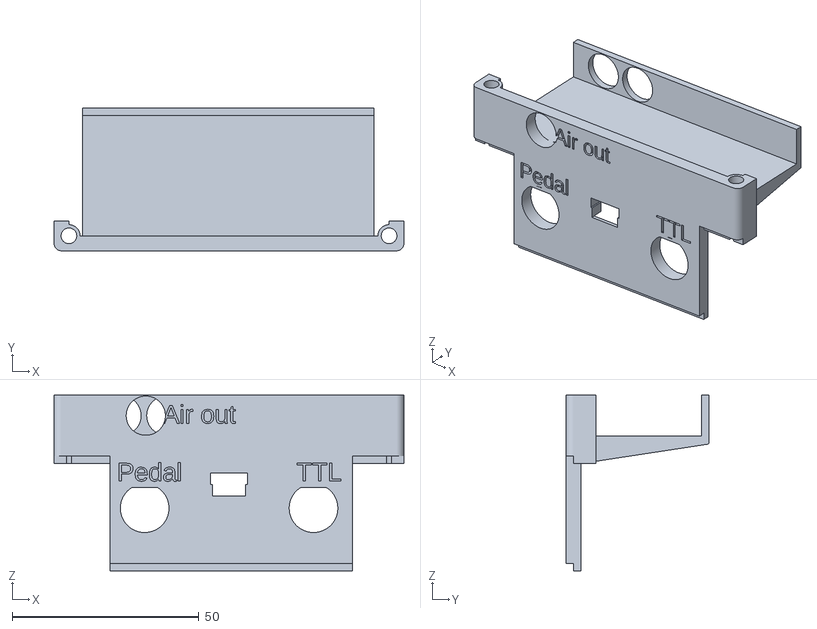
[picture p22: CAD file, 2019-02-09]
3D Designs/v1.3 - Customed PCB/STL Files/OpenSpritzer_Left.stl
93.8 x 38.2 x 47.1

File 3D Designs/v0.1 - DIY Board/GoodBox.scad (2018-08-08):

module GoodBox(XLen, YLen, ZLen, Thickness, Corner, Smoothness, HeadR, HeadD, NutR, NutD, ScrewR, ScrewD, LidOffset, SideBySide, Centering, Lid, Box) {

    // set the Lid Position
    LidXPos = SideBySide ? (Centering ? 0 : XLen/2) : (Centering ? 0 : XLen/2) ;
    LidYPos = SideBySide ? (Centering ? LidOffset + YLen : YLen/2 + YLen + LidOffset) : (Centering ? 0 : YLen/2) ;
    LidZPos = SideBySide ? (Centering ? 0 : Thickness/2) : (Centering ? LidOffset : Thickness/2 + LidOffset);

    // set box position
    BaseXPos = Centering ? 0 : XLen/2;
    BaseYPos = Centering ? 0 : YLen/2; 
    BaseZPos = Centering ? 0 : ZLen/2; 

    // produce the goods as requested!
    if (Box==true) {
        translate([BaseXPos, BaseYPos, BaseZPos])
        difference(){
            GoodBoxBase_add(XLen, YLen, ZLen, Thickness, Corner, Smoothness);
            GoodBoxBase_sub(XLen, YLen, Corner, Smoothness, NutR, NutD, ScrewR, ScrewD);
        }
    }
    
    if (Lid==true) {
        translate([LidXPos, LidYPos, LidZPos])
        difference(){
            GoodBoxLid_add(XLen,YLen, Thickness, Corner, Smoothness);
            GoodBoxLid_sub(XLen, YLen, Corner, ScrewR, Thickness, HeadR, HeadD, Smoothness);
        }
    }
}

module GoodBoxBase_add(XLen, YLen, ZLen, Thickness, Corner, Smoothness) {
        BasicBox( XLen,
                  YLen, 
                  ZLen, 
                  Thickness, Corner, Smoothness);

        CornerCylinder(-XLen/2 + Corner, -YLen/2 + Corner, ZLen, Corner, Smoothness);
        CornerCylinder(-XLen/2 + Corner,  YLen/2 - Corner, ZLen, Corner, Smoothness);
        CornerCylinder( XLen/2 - Corner, -YLen/2 + Corner, ZLen, Corner, Smoothness);
        CornerCylinder( XLen/2 - Corner,  YLen/2 - Corner, ZLen, Corner, Smoothness);
}


module GoodBoxBase_sub(XLen, YLen, Corner, Smoothness, NutR, NutD, ScrewR, ScrewD) {
      // Four corner screw holes
        ScrewHoleHex( -XLen/2 + Corner,
                      -YLen/2 + Corner,
                       0,
                       NutR, NutD, ScrewR, ScrewD, Smoothness);

        ScrewHoleHex( -XLen/2 + Corner,
                       YLen/2 - Corner,
                       0,
                       NutR, NutD, ScrewR, ScrewD, Smoothness);

        ScrewHoleHex(  XLen/2 - Corner,
                      -YLen/2 + Corner,
                       0,
                       NutR, NutD, ScrewR, ScrewD, Smoothness);


        ScrewHoleHex(  XLen/2 - Corner,
                       YLen/2 - Corner,
                       0,
                       NutR, NutD, ScrewR, ScrewD, Smoothness);
}

module GoodBoxLid_add(XLen,YLen, ZLen, Corner, Smoothness) {
        minkowski(){
            cube([ XLen - 2 * Corner, 
                   YLen - 2 * Corner, 
                   ZLen/2], true);
            cylinder(ZLen/2, Corner, Corner, true, $fn=Smoothness); 
    }
}

module GoodBoxLid_sub(XLen, YLen, Corner, ScrewR, ScrewD, HeadR, HeadD, Smoothness) {
      // Four corner screw holes
        ScrewHole(-XLen/2 + Corner,
                  -YLen/2 + Corner,
                   0,
                   ScrewR, ScrewD, HeadR, HeadD, Smoothness);

        ScrewHole(-XLen/2 + Corner,
                   YLen/2 - Corner,
                   0,
                   ScrewR, ScrewD, HeadR, HeadD, Smoothness);

        ScrewHole( XLen/2 - Corner,
                  -YLen/2 + Corner,
                   0,
                   ScrewR, ScrewD, HeadR, HeadD, Smoothness);

        ScrewHole( XLen/2 - Corner,
                   YLen/2 - Corner,
                   0,
                   ScrewR, ScrewD, HeadR, HeadD, Smoothness);
}

// x, y and z specify outer dimensions
module BasicBox(x, y, z, thickness, corner, smoothness) {
    translate([corner - x/2, corner - y/2, - z/2])
    difference() {
        $fn=smoothness;
        minkowski(){
            cube( [x-2*corner, y-2*corner, z-thickness], false );
            cylinder( thickness, corner, corner, false);
        }
        
        translate( [thickness, thickness, thickness] ) 
        minkowski(){
            cube( [x - 2*corner - 2*thickness, y - 2*corner - 2*thickness, z-thickness], false);
            cylinder(thickness, corner, corner, false);
        }
    }
}

module CornerCylinder(x, y, ZLen, Corner, Smoothness) {
        translate( [x, y , 0])
        cylinder(ZLen, Corner, Corner, true, $fn=Smoothness);
}

module ScrewHole( x, y, z, screwR, screwD, headR, headD, smoothness ){
    translate( [x, y, z]) 
    cylinder( screwD, screwR, screwR, true, $fn=smoothness );
    translate( [x, y, z + screwD/2 - headD/2]) 
    cylinder( headD, headR, headR, true, $fn=smoothness );
}

module ScrewHoleHex( x, y, z, nutR, nutD, screwR, screwD, smoothness){
    translate( [x, y, z]) 
    cylinder(screwD, screwR, screwR, true, $fn=smoothness);

    translate( [x, y, z - screwD/2 + nutD/2])
    cylinder(nutD, nutR, nutR, true, $fn=6);
}

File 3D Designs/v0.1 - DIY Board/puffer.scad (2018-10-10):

use <GoodBox.scad>;
tol = 0.2;

//Regulator- these are measurements taken from the regulator
RegHeight = 50.1;
RegWidth = 50.1;
RegLength = 52.75;
RegKnobDiam = 35.8 + tol;//35.7;
AirHoseInDiameter = 13.3 + tol;
AirHoseInYOffset = (36.95 + 48.05)/2 + .4;
AirHoseOutDiameter = 10.3 + tol;
//AirHoseOutYOffset = (15.78 + 5.72)/2; // (this one is port 1)
AirHoseOutYOffset = (13.49 + 19.18)/2; // (this one is port 2)
GaugeDiameter = 9.8 + tol;
GaugeYOffset = (13.2 + 22.72)/2 +.3;
CollarHeight = 9;

//solenoid - measurements taken from the solenoid.
SolLength=88.6;
SolBodyLength = 73.2;
SolWidth = 32.5;
SolHeight = 10.1;
SolRetWidth = 4;
SolRetOffsetX = 6.5;//5;
SolShelfDepth = 4;

// basic box params - size of the box and screw holes. Smoothness of corners etc.
Thickness = 1.5;
CornerR = 4;
XLen = 110; //external sizes
YLen = SolLength + 2*Thickness + 2*CornerR;
ZLen = RegHeight + Thickness;
Smoothness = 60;
HeadR = 2; 
HeadD = Thickness;
NutD =  ZLen/2;
NutR =  7/2; //6.5/2 too small;  //5 wayyy to big.
ScrewR = 1.6;
ScrewD = ZLen;

// control where lid appears relative to box. Probably best to leave as is because
// holes might not move in same way as lid.
LidOffset = 50;
SideBySide= false;
Centering= true;

// switch on lid and box independently.
Lid = false;
Box = true;

// sol derived quantities
SolYPosition = -YLen/2 + 2*CornerR;
SolShelfHeight  = ZLen - Thickness - 2 * SolHeight;
SolRetHeight = SolShelfHeight + SolHeight;

//Circuit board position and screw stand offs.
BoardYPosition = SolYPosition + SolShelfDepth + 2;
BoardEdgeX = 4.2;
BoardEdgeY = 4.2;
MountPointWidth = 38;//(36.34 + 38.5)/2;//(37.29 + 39.10)/2;
MountPointLength = (48.93 + 51.2)/2;//(54.82 + 56.78)/2;
MountPointHeight = 5;
MountPointInnerDiameter = 1.5;
MountPointOuterDiameter = 4;


// spacing betweeen holes
HoleSpacing = 7; // side panel
HoleSpacingFront = (XLen - Thickness - RegWidth/2 - RegKnobDiam/2)/3; // front panel

// Define cable hole sizes
USBHeight = 3.8 + tol;
USBWidth = 7.6 + tol;
USBWidth2 = 6.5 + tol;
BNCDiam = 9.3 + tol;
BNCFlatDiam = 8 + tol;
BNCFlatbitOffset = BNCDiam - BNCFlatDiam;
PotDiam = 9.8 + tol;
PotFlatDiam = 8.72 + tol;
PotFlatbitOffset = BNCDiam - BNCFlatDiam;
ToggleSwitchDiam = 6.1 + tol;
TogSwitchWidth = 11.5 + tol;
TogSwitchHeight = 12.8 + tol;

PowerJackWidth = 8.9 + tol;  //9
PowerJackHeight = 11.15 + tol; //11.25
PowerJackSupportDepth = 8.3 - Thickness;
PowerJackSupportHoleDiam = 2.1 + tol;
FootSwitchHoleDiam = 5.8 + tol;
LEDDiameter = 4.4 + tol;

// determine the position of the cables on the size panel.

// Z-Y offset of the USB hole from it's position relative to the circuit board.
USBYOffset = 22.31;//(11.62 + 13.74 + 26.87 + 29.01)/4//  (18.99 + 9.64)/2;//(18.99 + 9.64)/2; //measured from the mount point nearest arduino. controls the Y position of the four cable holes on the side panel.
USBZOffset = 17.2; // was (18.01 + 14.01)/2 // controls Z position of four cable holes on the size panel

// Y position of the center of the USB socket including its offset and position relative to circuit board
USBYPosition = BoardYPosition + BoardEdgeY + MountPointLength - USBYOffset + USBWidth/2;

// the position of the other cable holes in the side panel relative to the USB socket
BNCYPosition = USBYPosition + USBWidth/2 + HoleSpacing + BNCDiam/2;
PowerJackYPosition = SolYPosition + SolBodyLength + PowerJackWidth/2; 
FootswitchYPosition = USBYPosition - USBWidth/2 - HoleSpacing - BNCDiam/2;


//Regulator Y Position
RegYPosition = YLen/2 - 6.8;
RegSpacerDepth = YLen/2 - RegYPosition;
RegSpacerWidth = 6;

// call the function build the box
PicoSpritz();

// first the bits to add, then the bits to subtract.
module PicoSpritz()
{
    difference(){
        PicoSpritz_add();
        PicoSpritz_sub();
    }
      
}

// all the components to add
module PicoSpritz_add() {

    // Set up the basic good box
    GoodBox(XLen, YLen, ZLen, Thickness, CornerR, Smoothness, HeadR, HeadD, NutR, NutD, ScrewR, ScrewD, LidOffset, SideBySide, Centering, Lid, Box);
    
    if (Box==true) {
        // Regulator Spacer
        translate([-XLen/2 + Thickness + RegWidth, RegYPosition + RegSpacerDepth/2, Thickness/2]) cube([RegSpacerWidth, RegSpacerDepth, ZLen - Thickness], true);

        // Solenoid Shelf Back
        translate([XLen/2 - Thickness - SolWidth/2, SolYPosition + SolShelfDepth/2, -ZLen/2 + Thickness + SolShelfHeight/2]) cube([SolWidth, SolShelfDepth, SolShelfHeight], true);
        
        // Solenoid rear Retainer
        translate([XLen/2 - Thickness - SolWidth - SolRetWidth/2, SolYPosition + SolShelfDepth/2, -ZLen/2 + Thickness + SolRetHeight/2]) cube([SolRetWidth, SolShelfDepth, SolRetHeight], true);

        // Solenoid Shelf Front
        translate([XLen/2 - Thickness - SolWidth/2, SolYPosition + SolBodyLength - SolShelfDepth/2, -ZLen/2 + Thickness + SolShelfHeight/2]) cube([SolWidth, SolShelfDepth, SolShelfHeight], true);

        // Solenoid Front Retainer1
        translate([XLen/2 - Thickness - SolWidth - SolRetWidth/2 + SolRetOffsetX, SolYPosition + SolBodyLength + SolRetWidth/2, -ZLen/2 + Thickness + SolRetHeight/2]) cube([SolRetWidth , SolRetWidth, SolRetHeight], true);
        
        // Solenoid Front Retainer2
        translate([XLen/2 - Thickness - SolWidth - SolRetWidth/2, SolYPosition + SolBodyLength - SolShelfDepth/2, -ZLen/2 + Thickness + SolRetHeight/2]) cube([SolRetWidth, SolShelfDepth, SolRetHeight], true);
        
        // MountingPoints 
        // Rear Right
        translate([XLen/2 - Thickness - BoardEdgeX, BoardYPosition + BoardEdgeY, -ZLen/2 + Thickness + MountPointHeight/2]) cylinder(MountPointHeight, MountPointOuterDiameter/2, MountPointOuterDiameter/2, $fn=Smoothness, true);
        
        // Rear Left
        translate([XLen/2 - Thickness - BoardEdgeX - MountPointWidth, BoardYPosition + BoardEdgeY, -ZLen/2 + Thickness + MountPointHeight/2]) cylinder(MountPointHeight, MountPointOuterDiameter/2, MountPointOuterDiameter/2, $fn=Smoothness, true);

        // Front Right
        translate([XLen/2 - Thickness - BoardEdgeX, BoardYPosition + BoardEdgeY + MountPointLength, -ZLen/2 + Thickness + MountPointHeight/2]) cylinder(MountPointHeight, MountPointOuterDiameter/2, MountPointOuterDiameter/2, $fn=Smoothness, true);

        // Front Left
        translate([XLen/2 - Thickness - BoardEdgeX - MountPointWidth, BoardYPosition + BoardEdgeY + MountPointLength, -ZLen/2 + Thickness + MountPointHeight/2]) cylinder(MountPointHeight, MountPointOuterDiameter/2, MountPointOuterDiameter/2, $fn=Smoothness, true);

        // Power Jack Support vertical
        translate([XLen/2 - Thickness/2 - PowerJackSupportDepth/2, PowerJackYPosition - PowerJackWidth/2 - Thickness/2, -ZLen/2 + Thickness + MountPointHeight + USBZOffset ] ) 
        cube([PowerJackSupportDepth, Thickness, PowerJackHeight], true);
        
        // Power Jack Support Horiz
        translate([XLen/2 - Thickness/2 - PowerJackSupportDepth/2, PowerJackYPosition, -ZLen/2 + Thickness + MountPointHeight + USBZOffset - PowerJackHeight/2 - Thickness/2] ) 
        cube([PowerJackSupportDepth, PowerJackWidth, Thickness], true);
    }
    
    if (Lid==true) {
        // Lid Blocks for solenoid
        translate([XLen/2 - Thickness - SolWidth/2, SolYPosition + SolShelfDepth/2, LidOffset - SolHeight/2 - Thickness/2]) cube([SolWidth, SolShelfDepth, SolHeight], true);

        translate([XLen/2 - Thickness - SolWidth/2, SolYPosition + 3*SolBodyLength/4 - SolShelfDepth/2, LidOffset - SolHeight/2 - Thickness/2]) cube([SolWidth, SolShelfDepth, SolHeight], true);
    }        
}

// all the holes
module PicoSpritz_sub() {
    
    // Solenoid Lid Block trimming to allow Sol Retainer
    //translate([XLen/2 - Thickness - SolWidth - SolRetWidth/2 + SolRetOffsetX, SolYPosition + SolBodyLength + SolRetWidth/2, LidOffset - SolRetHeight/2 - Thickness/2]) cube([SolRetWidth , SolRetWidth, SolRetHeight], true);
    
    // Regulator Hole
    translate([-XLen/2 + Thickness + RegWidth/2, YLen/2 - Thickness/2, -ZLen/2 + Thickness + RegHeight/2])
    rotate(90, [1, 0, 0])
    cylinder(2*CollarHeight, RegKnobDiam/2, RegKnobDiam/2, $fn=Smoothness, true);
    
    // Regulator Block Simulator (Remove Space Size of Regulator.  Purpose is to chops off Corner to right depth...
    translate([-XLen/2 + Thickness + RegWidth/2, RegYPosition - RegLength/2, -ZLen/2 + Thickness + RegHeight/2])
    cube([RegWidth, RegLength, RegHeight], true );
    
    // Gauge Hole
    translate([-XLen/2 + Thickness + RegWidth/2, RegYPosition - GaugeYOffset, LidOffset] ) cylinder(Thickness, GaugeDiameter/2, GaugeDiameter/2, $fn=Smoothness, true);
    
    // LED Hole    
    translate([+XLen/2 - Thickness - RegWidth/2, RegYPosition - GaugeYOffset, LidOffset] ) cylinder(Thickness, LEDDiameter/2, LEDDiameter/2, $fn=Smoothness, true);
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

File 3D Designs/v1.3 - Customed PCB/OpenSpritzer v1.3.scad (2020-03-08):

/* 


        OpenSpritzer v1.3, an open hardware pressure ejection system.

This 3D file is designed for the OpenSpritzer project components and its customed PCB
Source : https://github.com/BadenLab/Openspritzer
This project is Open Source licensed, released under CERN OHL v1.2

by M.J.Y. Zimmermann, 2018.12.11
Baden Lab, CRPC, School of Life Sciences, University of Sussex, United Kingdom

                                                                                     */



// // // // // // // // // // // // // // // // // // // // // // // // // // // // //
/*                            ---  User Parameters  ---                             */
 
Wall = 2;           // Defines the wall thickness of the box
Smoothness = 360;    // Number of facets
tol = 0.1;          // Printing tolerance
TOL = 0.4;          // Component tolerance

sep = 5;            // x & y separation values for display function
zsep = 5;           // z separation values for display function

// // // // // // // // // // // // // // // // // // // // // // // // // // // //
// // // // // // // // // // // // // // // // // // // // // // // // // // // //
/*                               ---  Switches  ---                              */


// Parts to be printed
Bottom =  1;        // Lower Part of the box
Front =   1;        // Front Part of the box
Back =    1;        // Back Part of the box
Right =   1;        // Right Part of the box
Left =    1;        // Left Part of the box
Lid =     1;        // Top Part of the box


// Display part used for visualisation
Regulator = 10;     // Pressure Regulator
Solenoid = 10;      // Pressure Solenoid
PCB = 10;           // Custumed Printed Circuit Board


// // // // // // // // // // // // // // // // // // // // // // // // // // // //
// // // // // // // // // // // // // // // // // // // // // // // // // // // //
/*                        ---  Component Parameteres  ---                        */

//Hardware measurements

// M3
r_M3 = 3/2;
R_M3 = 4/2;
r_M3_nut = 6.44/2;
h_M3_nut = 2.3;
    
// M4
r_M4 = 4/2; //M4 screw radius 
R_M4 = 6.85/2; // M4 socket radius
r_M4_nut = 7.8/2; //M4 nut radius
h_M4_nut = 2.1; //M4 nut heigh
r_M6 = 6/2; //M6 screw radius

//Regulator- measurements taken from the regulator
x_Reg = 50.1+2*tol;
y_Reg = 52.75+2*tol;
z_Reg = 50.1+2*tol;
r_RegKnob = 35.8/2 + tol;
pos_y_Reg = 5 + r_RegKnob + TOL;
pos_z_Reg = 2 + r_RegKnob;
r_Gauge = 40/2;
GaugexOffset = (13.2 + 22.72)/2 +.3;
GaugeDiameter = 9.8/2 + tol;
AirHoseInxOffset = (36.95 + 48.05)/2 + .4-4.5+4.75;
r_AirHoseIn = (16)/2 + tol;
x_RegStop = 5;

r_AirHoseOut = 10.3/2 + tol;

//Main Box
x_Box = 85+2*TOL;
y_Box = 130 +2*TOL;
z_Box = z_Reg + 2*Wall + 2*TOL;

//Solenoid - measurements taken from the solenoid.
x_Sol = 33.5+Wall+2*tol;
x_Sol_Plat = x_Sol+3*Wall;
y_Sol= 73+2*tol;
z_Sol = 10+2*tol;
y_Sol_in = 17;
y_Sol_out1 = 10.5;
y_Sol_out2 = 22.5;
r_Sol = 10.3/2 + tol;

//PCB - measurements taken from the PBC footprint.
x_PCB = 85+2*tol;
y_PCB = 57.5+2*tol;
z_PCB = 1.6;
pos_z_PCB = 15-tol;
r_Platform = r_M4 + Wall; // holder for PCB radius
h_Platform = pos_z_PCB-z_PCB-tol; // holder for PCB height
pos_x_Platform1 = -x_Box/2 + TOL + r_Platform + 28.5;
pos_x_Platform2 = -x_Box/2 + TOL + r_Platform + 28.5 + 29;
pos_y_Platform1 = -y_Box/2 + TOL + r_Platform + 18;
pos_y_Platform2 = -y_Box/2 + TOL + 2*Wall + 18 + 36;


// DPDT switch
pos_y_DPDT = 20;
h_DPDT = 9.14/2+0.51;
r_DPDT = 4.75/2;

// Potentiometer
pos_y_Pot = 42.75;
h_Pot = 13/2;
r_Pot = 9.5/2;

// BNC
pos_x_BNC1 = 20;
pos_x_BNC2 = 65-1.75;
pos_z_BNC = 15.8/2;
h_BNC = 15.8/2;
r_BNC = 12.83/2;
cut_BNC = r_BNC-5.54;

// LED
r_LED = 4.5/2 + tol;

// Barrel Jack
h_Jack = 11.15 + tol;
y_Jack = 9.25 + 2*tol;
pos_y_Jack = 47.75;

// Mini USB
h_USB = 4 + tol+2;
USBWidth = 7.65 + 2*tol+2;
USBWidth2 = 6.75 + 2*tol+2;
pos_z_USB = 13.7-2.5;

// Power Switch
x_Switch = 20.5/2;//14;
y_Switch = 20;

// PCB holder screw positions
screw01 = [-x_Box/2+2*Wall,-y_Box/2+2*Wall,Wall];
screw02 = [-x_Box/2+2*Wall,y_Box/2+2*Wall,Wall];
screw03 = [x_Box/2+2*Wall,-y_Box/2+2*Wall,Wall];
screw04 = [x_Box/2+2*Wall,y_Box/2+2*Wall,Wall];

// Extra
z_Support = (z_Box-Wall-z_Sol-TOL-Wall-TOL)-(z_Box*2/3-Wall);
angle_Support =[0,90-atan(x_Sol_Plat/z_Support),0];

// // // // // // // // // // // // // // // // // // // // // // // // // // // //
/*                               ---  Display  ---                               */

if(Bottom==1){
    difference(){
        Puffer();
        Front_neg();
        Right_neg();
        Left_neg();
        Back_neg();
    }
}

if(Front==1){translate([sep,0,zsep]){
    difference(){
        intersection(){
            Puffer();
            Front();
        }
        Right_neg();
        Left_neg();
        translate([x_Box/2+2*Wall-TOL,-y_Box/2+2*Wall+TOL+pos_y_DPDT,pos_z_PCB+h_DPDT])rotate([0,90,0])cylinder(r=r_DPDT,h=2*Wall+TOL,$fn=Smoothness);
    }
}}
if(Back==1){translate([-sep,0,zsep]){
    difference(){
        intersection(){
            Puffer();
            Back();
        }
        Right_neg();
        Left_neg();
    }
}}
if(Right==1){translate([0,sep,2*zsep]){
    intersection(){
        Puffer();
        Right();
    }
}}

if(Left==1)translate([0,-sep,2*zsep]){
    intersection(){
        Puffer();
        Left();
    }
    difference(){
        Solenoid_Platform();
        Solenoid();
    }
}

if(Lid==1){translate([0,0,3*zsep+tol]){
    difference(){
        Lid();
        Logo();
        LED();
        Title();
        Screw_hole();
        Regulator();
        Power_Switch();
    }
    difference(){
        Box();
        Top_negative();
    }
}}  

if (Regulator==1)Regulator();
if (Solenoid==1)Solenoid(); 
if (PCB==1)PCB();
    

// // // // // // // // // // // // // // // // // // // // // // // // // // // //
/*                               ---  Modules  ---                               */


// // // // // // // // // // // // Box Modules // // // // // // // // // // // //
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

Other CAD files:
3D Designs/v1.3 - Customed PCB/STL Files/OpenSpritzer_Back.stl
3D Printing Files/v1.3 - Customed PCB/OpenSpritzer v1.2.scad

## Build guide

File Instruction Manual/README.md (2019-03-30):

<p align="right">
<h1 align="center">Instruction Manual</h1></p>
<h1 align="center">OpenSpritzer v1.3</h1>

***

## Overview

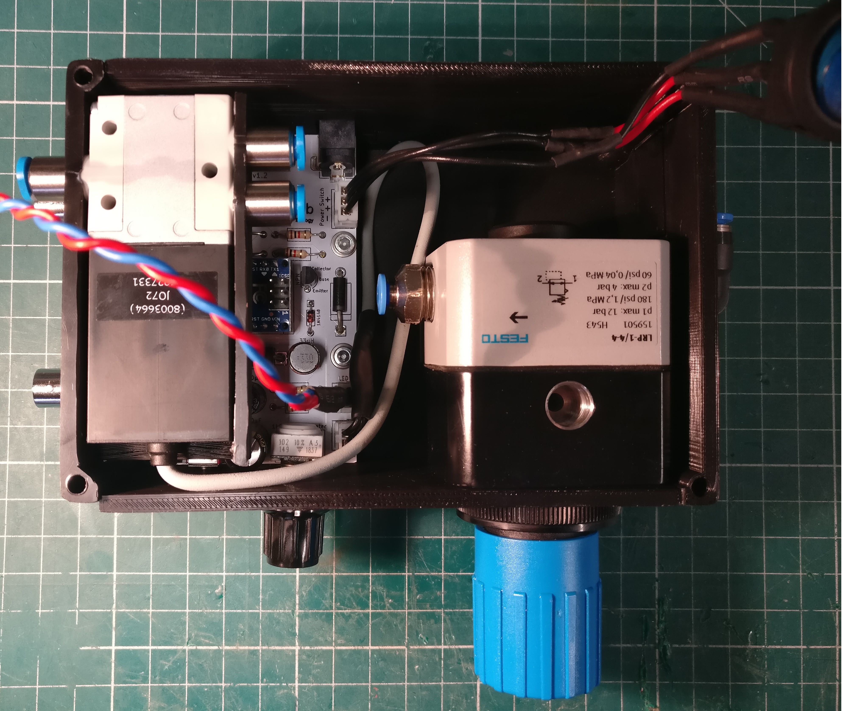
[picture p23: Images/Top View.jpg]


This document contains detailed assembly instructions, a software guideline and includes a parts list.

 The Arduino code and 3D printing files (SCAD and STL) can be downloaded [here](https://github.com/BadenLab/Openspritzer/tree/master/3D%20Designs/v1.3%20-%20Customed%20PCB), and further modified to fit customise purposes. The purpose of the device is to regulate the pressure and duration of a puff of compressed air. Typically, the output port is connected to a glass puffer pipette which has been drawn into a sharp point with a narrow (2-3μm) diameter pore.

The device consists of a circuit board, a solenoid valve, a pressure regulator with a gauge and various interface, off-the-shelf, components.

The device is here shown without its covering lid. The pressure regulator is mounted on the right and attached to the front panel via a retaining threaded ring that comes with the regulator. The printed circuit board (PCB) is mounted onto attachment points on the bottom of the box. There is a platform supports on which the solenoid can rest above the circuit board and a LED can be attached to a mount-point on the lid.

***

- [Assembling OpenSpritzer](#Assembly)
- [Programming OpenSpritzer](#Programming-the-Spritzer)
- [Operating the Stimulator](#Operating-the-Stimulator)

***

## Assembly

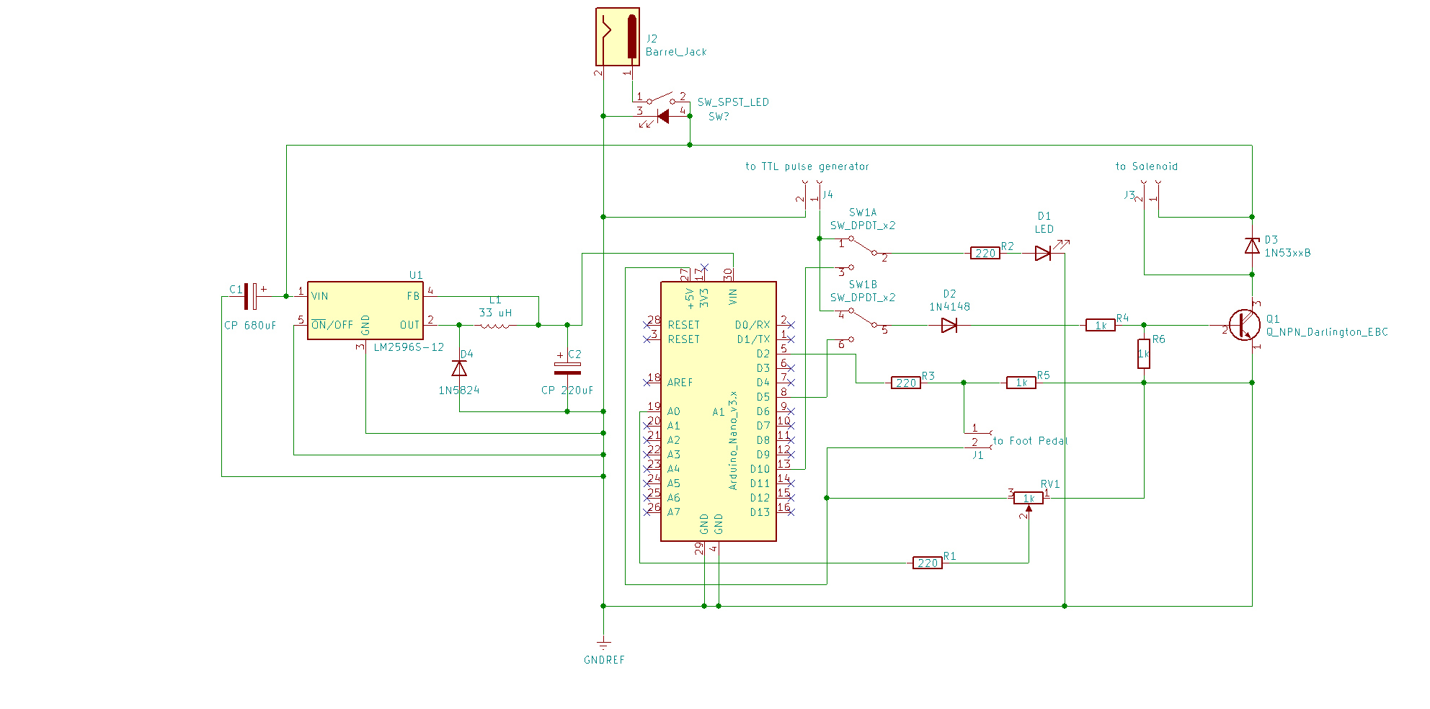
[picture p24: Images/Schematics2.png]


<p align="center"><h4 align="left">1 – Obtaining the custom-designed PCB</h4></p>

From the GitHub repository, one can find the [gerber.zip folder]https://github.com/BadenLab/Openspritzer/tree/master/PCB) needed to order the PCB to any manufacturer company (i.e. https://jlcpcb.com).

Ordering a minimum of 5 units should not cost more than £10. Gerber files were designed with [KiCad 5.0](http://kicad-pcb.org/).

Schematics and PCB footprint can be downloaded and modified from the same repository if need be.

****

<p align="center"><h4 align="left">2 – Soldering the custom-designed PCB</h4></p>


The board is self-explanatory and should not take more than an hour to solder

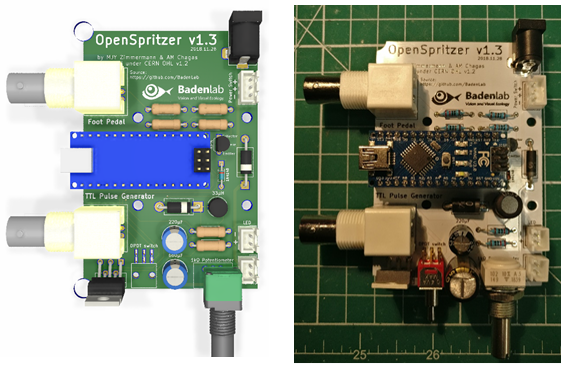
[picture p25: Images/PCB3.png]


***

<p align="center"><h4 align="left">3 – Printing the Spritzer box</h4></p>


[STL files](https://github.com/BadenLab/Openspritzer/tree/master/3D%20Designs/v1.3%20-%20Customed%20PCB/STL%20Files) can be found on the GitHub repository and print directly if the user wishes to go for the default design (4 stimulation LEDs + 4 proxy LEDs) and [BoM](https://github.com/BadenLab/Openspritzer/blob/master/Bill%20of%20Materials/BOM.csv).

However, [SCAD files](https://github.com/BadenLab/Openspritzer/blob/master/3D%20Designs/v1.3%20-%20Customed%20PCB/OpenSpritzer%20v1.3.scad) are also available and easily adjustable for personalised design.

We used [OpenSCAD](www.openscad.com) to design the stimulator box. The tolerance of the printer can be adjusted in the “USER Parameters” section of the script (tol =0.1; by default, this value is used for Prusa MK3 and Ultimaker 2). Each component can be displayed/design individually in the “Switches” section. Variables such as LED number (4 by default) and the potentiometer board dimensions can be adjusted in the “Component Parameters” section.

The PCB is screwed to the “Bottom” part of the box by using M3 screws and nuts. The potentiometer board adjusts itself with the “Back” part of the box, and the trimmers should adapt to their respective holes exactly.

All part should fit tightly together and are maintained together by 4 M3*50mm socket screws.

***

<p align="center"><h4 align="left">4 – Connecting the Spritzer</h4></p>

Connect an air compressor to the “Air In” port via the L-shaped adaptor.

The output airhose must be connected to the “Air Out” port.

A good pressure for sharp crisp pulses, which helps the solenoid to close again, is 1.4 bar (20 psi). Important: When first connecting high-pressure air to Openspritzer, e.g. from a compressor or air-tank, make sure that the Openspritzer gauge is near zero. A too-high line pressure (>>1.4 bar) risks irreversibly damaging the solenoid.
The stimulator must be powered with a 24v power supply. The Arduino Nano is powered through an internal voltage step-down regulator (24 to 5v). And does not need to be connected to be connected through a mini-USB cable once code has been uploaded.

For convenience in darkened circumstances the LED will also illuminate whenever the 5v line is high.

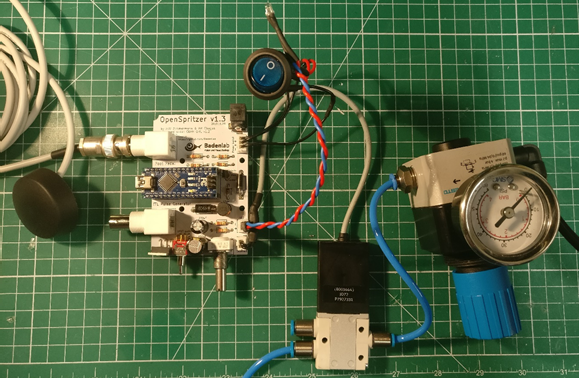
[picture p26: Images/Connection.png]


The foot pedal and/or the TTL cable(s), once soldered to a BNC male connector should be connected on the left side of the box to their appropriate BNC female connector. To operate with a footswitch the DPDT must be placed in the "Pedal" position. It is not necessary to use the Arduino to operate the solenoid if you have a convenient method for producing 5v TTL pulses, such as PulseQ electrophysiology package (Funetics) running on Igor Pro (Wavemetrics) in conjunction with the ITC 1600. To use TTL pulses ensure the DPDT switch is in the “TTL” position. Whenever the 5v line is high the solenoid will open and release compressed air from the output valve.

Attaching a computer at operation time allows for dynamic reprogramming of the Arduino during experimentation, which could be very useful. E.g. resetting the base time unit.
To operate the unit, press the foot-button and after 400 milliseconds a puff of a predefined duration will occur. The LED will illuminate during the puff to give visual confirmation that the puff has occurred. The duration of the puff can be changed by adjusting the potentiometer.

When the potentiometer is changed Openspritzer goes into a monitoring mode during which time the LED is lit and indicate the new time duration.

***

## Programming the Spritzer

1-	Download and install [Arduino environment](www.arduino.org) on a computer.

2-	Close Arduino and open the Openspritzer arduino file from the [Arduino Code folder](https://github.com/BadenLab/Openspritzer/blob/master/Arduino%20Code/Openspritzer/Openspritzer.ino).

3-	From the “Tools” tab: Select from “Boards” the “Arduino nano”.	From “Processor”, select ATM328P (If you're using an arduino clone or an old official board, select ATM328P (Old Bootloader)). From “Port”, select the computer port to which the Arduino is connected (if doubt, unplug, replug and observe the choices differences). If the Arduino is not recognised, check the driver installation (if you're using a clone, check the processor datasheet of your model), then check the mini USB cable.

4-	Compile and Upload the code by clicking on the arrow button on the top left.

5-	The Spritzer is ready to be used.

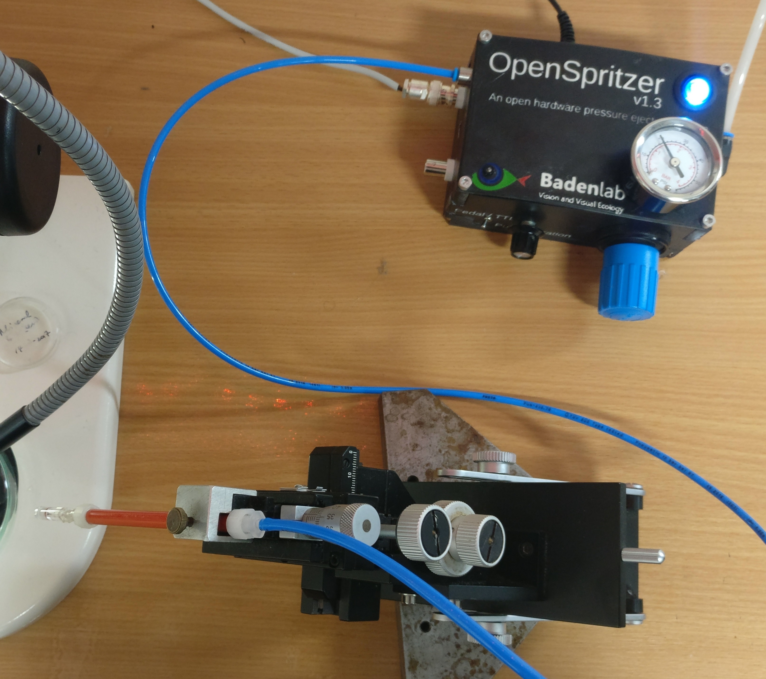
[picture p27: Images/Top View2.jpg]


***

The code can be modified and uploaded as many times as you like. The way the Openspritzer code has been constructed allows simple modification of key parameters such as the base unit of time and are listed in supporting table 2.

<h4> IMPORTANT</h4>: The first time that the Arduino is used the POT_LOW and POT_HIGH parameters should be measured. A Serial.println statement is included in the code to allow monitoring of this value over the serial port. To measure these values, open the serial port monitoring window in the Arduino programming environment (magnifying lens, top right corner) and then sweep the potentiometer from low to high. The two parameters POT_HIGH and POT_LOW should be initialised to the highest values and lowest values observed in the monitoring window output (usually those should be 0 and 1023). This is used in the calculations of the pulse duration and will vary from Openspritzer to Openspritzer depending on the precise value of the potentiometer resistance.

The monitoring algorithm relies on the PotNoise parameter to decide whether or not the potentiometer has settled. To set PotNoise, monitor the serial port output during the analog monitoring procedure (described above) and find the PotValue measured by the analogRead command. PotNoise should be larger than any fluctuations in the PotValue when it is not being altered. During testing, depending on which power supply was used, it was found that a reasonable value for PotNoise was 5.

Next the user assigns a time to the minimum and maximum potentiometer value by modifying PULSE_LOW and PULSE_HIGH. Those value are in milliseconds. PULSE_LOW will correspond to the minimum air puff duration when the potentiometer is turn all the way down, and reciprocally for PULSE_HIGH. By default those values are 10 and 1000 ms.
Finally, the PULSE_Delay is to be defined. This value allows some time for the user to release the button before applying the next pulse. This value can be adjusted to give rapid or spread pulses, however we found that for the average user, a value of 500ms is sufficient.

The user is obviously free to write any code they wish to monitor the foot button, read the potentiometer, blink the LED or operate the solenoid.

***

This project is licensed under the [GNU General Public License v3.0](https://github.com/BadenLab/Openspritzer/blob/master/LICENSE)

***

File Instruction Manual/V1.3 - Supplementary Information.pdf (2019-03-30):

## Supplementary Material

## (Revised Version for the v1.3 Printed Circuit Board), by MJY Zimmermann

## Openspritzer: an open hardware pressure ejection system for reliably delivering picolitre volumes

Forman, C.J.1,4§, Tomes, H.2, Mbobo, B.2, Baden, T1,3,4§., Raimondo, J.V.2,4§

Affiliations:
1) School of Life Sciences, University of Sussex, United Kingdom
2) Division of Physiology, Department of Human Biology, Neuroscience Institute and Institute of Infectious Disease and Molecular Medicine, Faculty of Health Sciences, University of Cape Town, Cape Town, South Africa
3) Institute for Ophthalmic Research, University of Tuebingen, Germany
4) TReND in Africa gUG (www.TReNDinAfrica.org)

§Correspondence: C.F.: chrisforman@cantab.net, T.B.: t.baden@sussex.ac.uk, J.V.R.: joseph.raimondo@uct.ac.za

Command duration is correlated to dosage


Supplementary Figure S1: The integrated area for each puff plotted against the command duration. The area under the puff profile is proportional to the dosage. Command duration and dosage are strongly correlated, regardless of the details of the puff profile over time.

Overview

This document contains detailed assembly instructions and an operation manual for Openspritzer and also includes a parts list. The Arduino code and 3D printing files for the exterior casing are provided and may be downloaded at https://github.com/BadenLab/Openspritzer. The purpose of the device is to regulate the pressure and duration of a puff of compressed air. Typically, the output port is connected to a glass puffer pipette which has been drawn into a sharp point with a narrow (<2-3 μm) diameter pore.
The device consists of a circuit board, a solenoid valve, a pressure regulator with a gauge and various interface components.

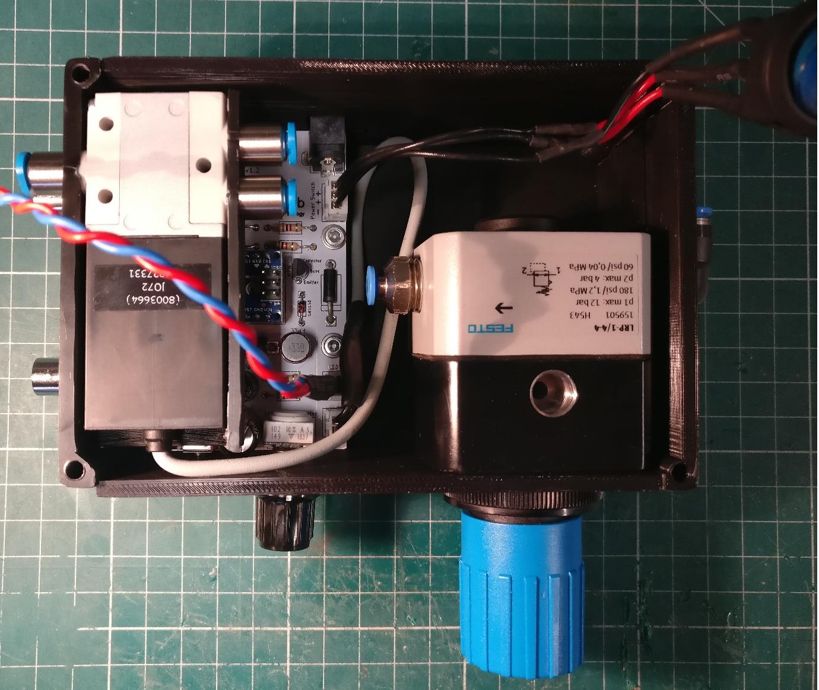
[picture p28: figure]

Supplementary Fig. S2: The device is shown without its covering lid. The pressure regulator is mounted on the right and attached to the front panel via a retaining threaded ring that comes with the regulator. The printed circuit board (PCB) is mounted onto attachment points on the bottom of the box. There is a platform supports on which the solenoid can rest above the circuit board and a LED can be attached to a mount-point on the lid.

Parts List
Supplementary Table 1 has an exhaustive list of parts, suppliers and prices, allowing calculation of the total cost of parts, which is between £320 and £360 at submission, depending on how much of the full system one chooses to include. Much of the circuitry e.g. the Arduino, footswitch and toggle switch is purely for convenience. A core functional system consists of the regulator, solenoid and a much simpler control circuit under TTL pulse control. The simpler minimal circuit is indicated in the construction instructions below and consists of the branch of the circuit containing the transistor.
In addition, prices are highly variable depending on local availability of components. For example, the single most expensive component when we assembled ours was the regulator which cost £180 at the time. However, we subsequently found the same regulator for $43 in a different country. If one is prepared to shop around, we estimate that a functional Openspritzer without add-ons could be constructed for as little as £175. If one has all the components it takes approximately 1 hours to construct a full Openspritzer depending on experience and excluding the print time for the case and lid.
Frequently components only come in bags of 10 or 50 so if one only intends to fabricate a single device there may be an additional overhead of extra parts, depending on the flexibility of your supplier. For example, ours cost £360 for the parts actually included in the device, but we paid £495 in total and now have some spare components for additional units.
Name | Manufacturer | Order ID | Retailer | Quantity Observation 1 | Observation 2
Solenoid (either 2 ms or 7 ms model) | FESTO | MHE2-M1SH-3/2G-M7-K-RR | Kiowa | 1 Pneumatics | 2 ms response + cable
Precision pressure regulator | FESTO | LRP-1/4-4 | RS | 1 Pneumatics | 0.05 to 4.0 bar
Gauge | FESTO | MAP-40-4-1/8-EN | Kiowa | 1 Pneumatics | 0.0 to 4.0 bar, 1/8 inch thread
Push-in (6 mm) to thread (1/4") | FESTO | QSL-1/4-6 | RS | 1 Pneumatics | 6 mm to 1/4 inch
Push-in (4 mm) to thread (1/4") | FESTO | QS-1/4-4 | RS | 1 Pneumatics | 4 mm to 1/4 inch
Push-in (4 mm) to thread (M7) | FESTO | QSM-M7-4-I | RS | 2 Pneumatics | 4 mm to M7 thread
4mm OD plastic tubing | FESTO | PUN-4x0.75 | RS | 12 cm Pneumatics | 4 mm OD and 10 bar
PicoNozzle Kit | World Precision Instrument | 5430 - x | WPI | 1 Pneumatics | for 1.0 / 1.2 / 1.5 / 2.0 mm glass pipettes
Arduino Nano | Arduino | | RS | 1 Electronics | nano
PCB socket | Samtec | SSW-116-02-G-S | RS | 2 Electronics | 1 row, 15 pin
Darlington pair NPN transistor | Fairchild | KSP 13BU | Farnell | 1 Electronics | Ic = 500 mA, Vces = 30 V
1 k? variable resistor | Vishay | 249FGJSPXB25102KA | RS | 1 Electronics | panel mount
Knob for variable resistor | RS Online | 783-0192 | TE
| | | Connectivity | 1 Electronics | 6.35mm shaft radius
DPDT switch | Multicomp | 2MD3T2B2M6RE | Farnell | 1 Electronics | ON-(OFF)-ON panel mount
SPST footswitch | RS Online | 335-319 | RS | 1 Electronics | push-to-contact

24V DC desktop PSU 2.1 mm jack | RS Online | 436-058 | RS | | 1 Electronics | 24 V dc 1 A
2.1 mm right angle DC socket | RS Online | 884-0957 | RS | | 1 Electronics | 2.1 mm right angle
24 V Zener Diode | Semiconductor | 1N5359BG | Farnell | | 1 Electronics | 24V
1N4148 signal diode | Fairchild | 1n4148 | Farnell | | 1 Electronics | 24V
1 k? resistor | Digikey | CF14JT1K00CT-ND | Digikey | | 3 Electronics | 1 k? through hole resistor
220 ? resistor | Digikey | CF14JT220RCT-ND | Digikey | | 3 Electronics | 220 ? through hole resistor
Voltage step-down regulator | RS Online | 533-3743 | RS | | 1 Electronics | 5V, 3A
Capacitor 680 µF | RS Online | 526-1569 | RS | | 1 Electronics | 24V minimum
Capacitor 220 µF | RS Online | 526-1480 | RS | | 1 Electronics | 24V minimum
Diode 1N5824 | RS Online | 714-6819 | RS | | 1 Electronics | 24V minimum
Inductor 33 µH | Bourns | RLB0914-330KL | Farnell | | 1 Electronics
3 mm LED | Digikey | 350-1557-ND | Digikey | | 1 Electronics | 3mm round, throughhole, grn
Mount for 3 mm LED | Digikey | 67-1330-ND | Digikey | | 1 Electronics | 3mm panel mount
BNC coaxial connectors | TE Connectivity | 1-1337542-0 | Farnell | | 2 Electronics | Right angle jacks, 50ohm
Cable Mount BNC Connector | RS Online | 546-3721 | RS | | 1 Electronics | Plug Crimp Termination
2 way JST Female Connector Housing | RS Online | 820-1611 | JST | | 2 Electronics
3 way JST Female Connector Housing | RS Online | 820-1614 | JST | | 1 Electronics
2 way JST PCB header | RS Online | 820-1554 | JST | | 2 Electronics
3 way JST PCB header | RS Online | 820-1557 | JST | | 1 Electronics
2 distinc colour wires | RS Online | 331-862 | RS | 20 cm | Electronics | 20 AWG
Cable shrink | RS Online | 170-6377 | RS | 5 cm | Electronics | Shrunk diameter 1.2 mm
Rocker LED switch | | | Ebay | | 1 Electronics | Round Switch / 3 pins
M3 x 10mm screw | RS Online | 660-4636 | RS | | 4 Mechanical | M3 x 10 Hex socket cap
M3 nut | RS Online | 122-4400 | RS | | 4 Mechanical | M3 nuts
M4 x 50mm Hex Socket Cap Screws | RS Online | 304-4592 | RS | | 4 Mechanical | M4 x 50
M4 nut | RS Online | 189-579 | RS | | 4 Mechanical | M4 nuts
Supplementary Table T1: Parts schedule for Openspritzer

Assembling the Stimulator

1 – Obtaining the custom-designed PCB

From the GitHub repository (https://github.com/BadenLab/Openspritzer/PCB), one can find the gerber.zip folder needed to order the PCB to any manufacturer company (i.e. https://jlcpcb.com). Ordering a minimum of 5 units should not cost more than £10. Gerber files were designed with KiCad
5.0. Schematics and PCB footprint can be downloaded and modified from the same repository if need be (Fig. S3).

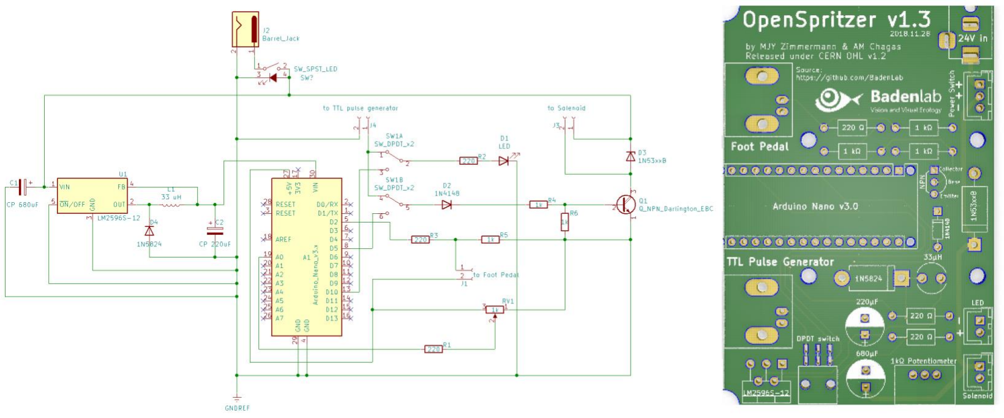
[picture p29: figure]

Supplementary Fig. S3: Schematics representing the device circuitry. The 24V power (J2) supply directly the solenoid valve which is controlled by an Arduino nano (A1), itself powered by a voltage regulator (U1). A potentiometer (RV1) value is read by the Arduino and sends a pulse in turn to the NPN transistor (Q1) which then connects the solenoid to the ground, activating it. A DPDT switch (SW1) allows the user to switch from a manual to a TTL control mode (left). Custom made PCB designed to fit the v1.3 custom box (right).

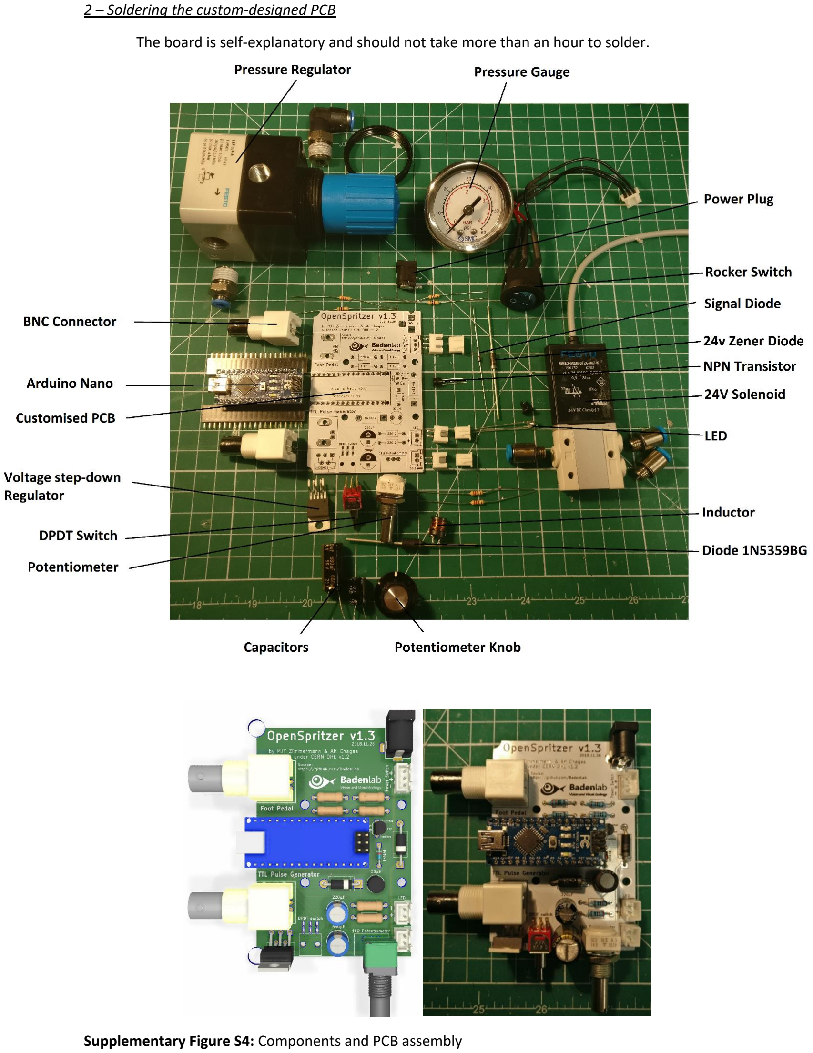
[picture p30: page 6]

2 – Soldering the custom-designed PCB

The board is self-explanatory and should not take more than an hour to solder.

Supplementary Figure S4: Components and PCB assembly

3 – Printing the Stimulator box

STL files can be found on the GitHub repository and print directly. However, SCAD files are also available and easily adjustable for personalised design.

We used OpenSCAD (freely available at www.openscad.com) to design the stimulator box. The tolerance of the printer can be adjusted in the “USER Parameters” section of the script (tol =0.1; by default, this value is used for Prusa MK3 and Ultimaker 2). Each component can be displayed/design individually in the “Switches” section. Variables can be adjusted in the “Component Parameters” section.

The PCB is screwed to the “Bottom” part of the box by using M3 screws and nuts.

All part should fit tightly together and are maintained together by 4 M3*50mm socket screws.

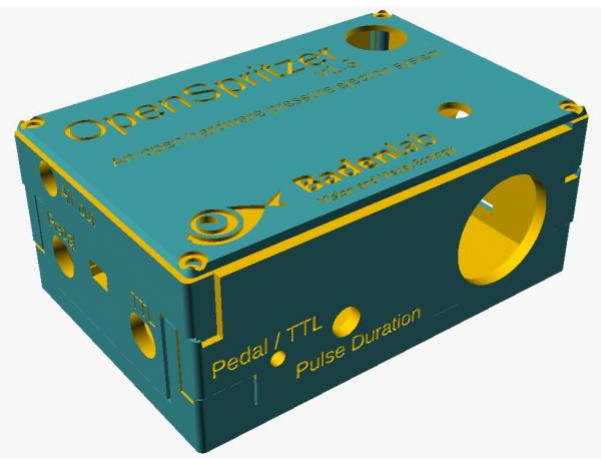
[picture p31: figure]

Supplementary Figure S5: Rendering of the custom design 3D printing box that fits exactly the custom PCB and the Spritzer components.

4 – Connecting the Spritzer

Connect an air compressor to the “Air In” port via the L-shaped adaptor.

The output airhose must be connected to the “Air Out” port.

A good pressure for sharp crisp pulses, which helps the solenoid to close again, is 1.4 bar (20 psi). Important: When first connecting high-pressure air to Openspritzer, e.g. from a compressor or air-tank, make sure that the Openspritzer gauge is near zero. A too-high line pressure (>>1.4 bar) risks irreversibly damaging the solenoid.

The stimulator must be powered with a 24v power supply. The Arduino Nano is powered through an internal voltage step-down regulator (24 to 5v). And does not need to be connected to be connected through a mini-USB cable once code has been uploaded.

For convenience in darkened circumstances the LED will also illuminate whenever the 5v line is high.

The foot pedal and/or the TTL cable(s), once soldered to a BNC male connector should be connected on the left side of the box to their appropriate BNC female connector. To operate with a footswitch the DPDT must be placed in the "Pedal" position. It is not necessary to use the Arduino to operate the solenoid if you have a convenient method for producing 5v TTL pulses, such as PulseQ electrophysiology package (Funetics) running on Igor Pro (Wavemetrics) in conjunction with the ITC 1600. To use TTL pulses ensure the DPDT switch is in the “TTL” position. Whenever the 5v line is high the solenoid will open and release compressed air from the output valve.

Attaching a computer at operation time allows for dynamic reprogramming of the Arduino during experimentation, which could be very useful. E.g. resetting the base time unit.

To operate the unit, press the foot-button and after 400 milliseconds a puff of a predefined duration will occur. The LED will illuminate during the puff to give visual confirmation that the puff has occurred. The duration of the puff can be changed by adjusting the potentiometer.

When the potentiometer is changed Openspritzer goes into a monitoring mode during which time the LED is lit and indicate the new time duration.

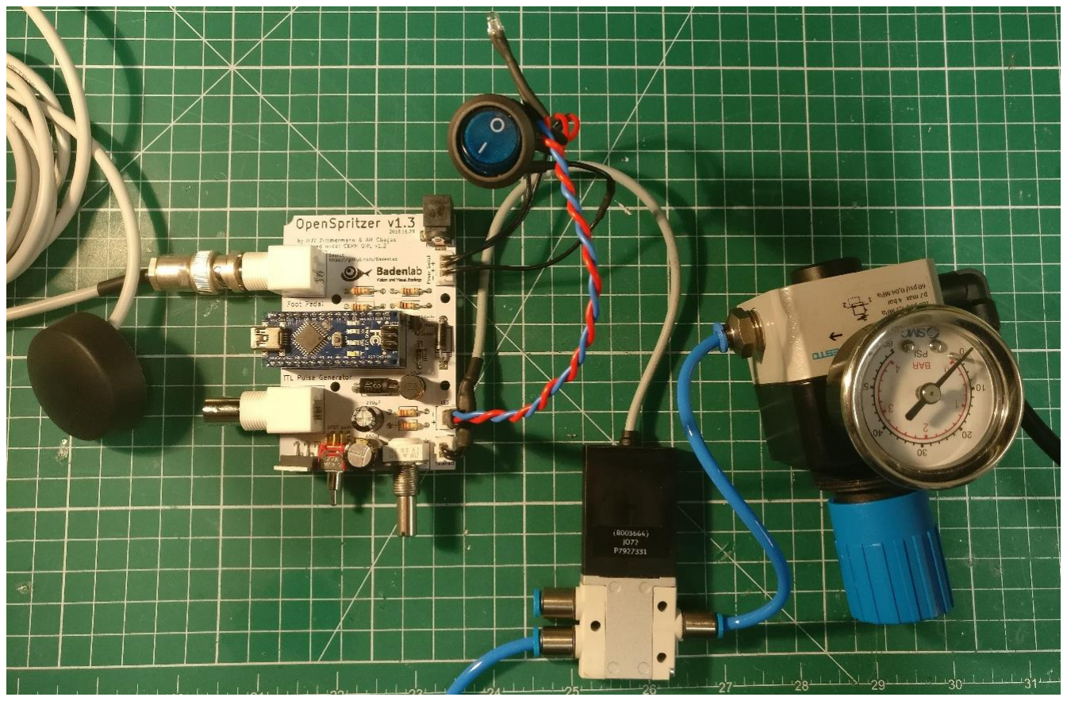
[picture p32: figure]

Supplementary Figure S5: The above picture shows the connection and arrangement between the custom PCB and all components.

5 - Programming the Arduino on board Openspritzer
Once Openspritzer is assembled the Arduino must be programmed: Download and install Arduino programming environment on your computer (www.Arduino.org).
Open the Openspritzer.ino code which is included in the Supplementary Materials.
Compile and upload code to the Openspritzer by connecting the USB port of Openspritzer to the USB port of your computer and by clicking on the "Upload" icon in the top left corner of the screen.
Code can be modified and uploaded as many times as you like. The way the Openspritzer code has been constructed allows simple modification of key parameters such as the base unit of time and are listed in supporting table 2.
IMPORTANT: The first time that the Arduino is used the POT_LOW and POT_HIGH parameters should be measured. A Serial.println statement is included in the code to allow monitoring of this value over the serial port. To measure these values, open the serial port monitoring window in the Arduino programming environment (magnifying lens, top right corner) and then sweep the potentiometer from low to high. The two parameters POT_HIGH and POT_LOW should be initialised to the highest values and lowest values observed in the monitoring window output (usually those should be 0 and 1023). This is used in the calculations of the pulse duration and will vary from Openspritzer to Openspritzer depending on the precise value of the potentiometer resistance.

The monitoring algorithm relies on the PotNoise parameter to decide whether or not the potentiometer has settled. To set PotNoise, monitor the serial port output during the analog monitoring procedure (described above) and find the PotValue measured by the analogRead command. PotNoise should be larger than any fluctuations in the PotValue when it is not being altered. During testing, depending on which power supply was used, it was found that a reasonable value for PotNoise was 5.

Next the user assigns a time to the minimum and maximum potentiometer value by modifying PULSE_LOW and PULSE_HIGH. Those value are in milliseconds. PULSE_LOW will correspond to the minimum air puff duration when the potentiometer is turn all the way down, and reciprocally for PULSE_HIGH. By default those values are 10 and 1000 ms.

Finally, the PULSE_Delay is to be defined. This value allows some time for the user to release the button before applying the next pulse. This value can be adjusted to give rapid or spread pulses, however we found that for the average user, a value of 500ms is sufficient.

The user is obviously free to write any code they wish to monitor the foot button, read the potentiometer, blink the LED or operate the solenoid.

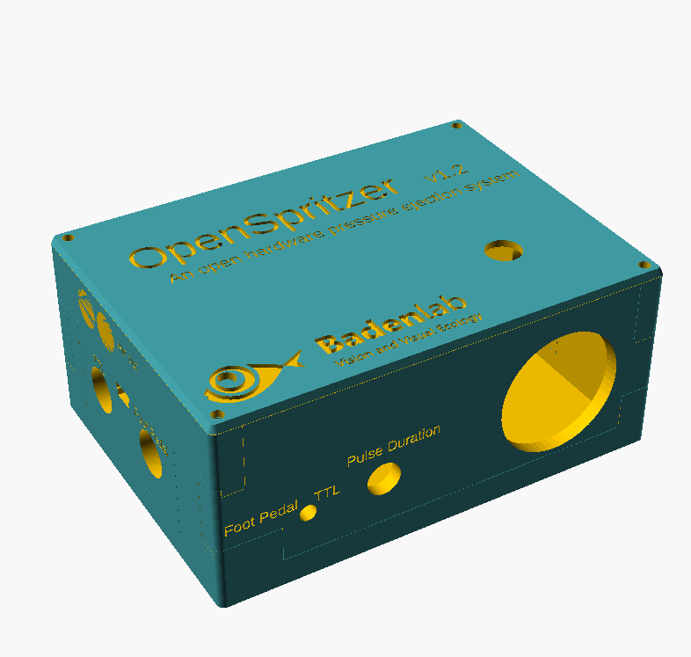
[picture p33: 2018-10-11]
Images/3d print2.png

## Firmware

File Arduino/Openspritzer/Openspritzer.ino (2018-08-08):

const int TIMEUNIT = 100;    // Base Time Unit in milliseconds.
const int POT_VALUE_LOW = 0; // Lowest value available from the pot.
const int POT_VALUE_HIGH = 1023; // Highest value available from the pot (measured value). Can make this higher by reducing resistor value in series with pot, but go below 125 Ohms and current will exceed 40 mA max on Analog pin.
const int SENSITIVITY = 10; // Number Of allowed settings of Potentiometer is (Sensitivity) (1 based...) make sure that Pot range = (High-low)/sensitivity isn't smaller than potnoise
const int POT_NOISE = 5; // Amplitude of fluctuations in the Pot Value when it is static. Measured value.some power supplies are noisier than others.
const int STABILITY_TIME = 500; // number of milliseconds for which stability must be achieved when adjusting pot to accept new value.
const int MONITOR_DELAY = 100; // delay between loops for analog monitoring cycles - allows user time to adjust pot a significant amount between loops.
const int PAUSE_BEFORE_BLINK = 500; // number of milliseconds to pause before starting blinks.
const int BLINK_ON_DURATION = 100; // this combo seems to work nicely. 
const int BLINK_OFF_DURATION = 250;
const int NUM_PROGRAMMED_PULSES = 28; // number of pulses to implement in hard coded sequence
int PROGRAMMED_SEQUENCE[28] = {1, 2, 3, 4, 5, 6, 7, 8, 9, 10, 20, 30, 40, 50, 60, 70, 80, 90, 100, 200, 300, 400, 500, 600, 700, 800, 900, 1000}; // sequence of pulses in ms
const int PROGRAMMED_PULSE_DELAY = 2000; // delay between pulses.
const int MONITOR_FOOTSWITCH_PERIOD =400; // seems long enough for a double click. Can get a triple in there too.
const int FOOTBUTTONDELAY = 1000; // liberally dispersed throughout the code to give time for people to release the button.


// Set up the pins
const int D_FootButtonPin = 2;
const int D_LEDPin = 10;
const int A_PotPin = 0;
const int D_SolenoidPin = 5;

// Declare global variables - These are designed to be adjusted simultaneously using the SetPulseDuration function.
int PulseDuration = 0;
int PotSetting = 0;
int PotValue = 0;
int numButtonClicks=0;

void setup() {

  //initialiase serial port for output messages
  Serial.begin(9600);
  
  // initialize the pins
  pinMode(A_PotPin, INPUT);
  pinMode(D_FootButtonPin, INPUT);
  pinMode(D_LEDPin, OUTPUT);
  pinMode(D_SolenoidPin, OUTPUT);

  // set initial conditions on pins.
  digitalWrite(D_SolenoidPin, LOW);
  digitalWrite(D_LEDPin, LOW);
    
  // monitor the pot to make sure it is stable, includes lighting the LED to show aliveness...
  MonitorAnalog();
  SetPulseDuration(); // set the initial pulse duration and report new values over serial link.
  LEDBlinks(); // blink the LED to indicate the pot Setting.
}

// function reads the potentiometer and populates the three global variables PotValue, PotSetting and PulseDuration
// with mutually consistent values. These global values are not intended to be set using any other function.
void SetPulseDuration() {
  PotValue = analogRead(A_PotPin);
  
  // compute the Potentiometer Setting as an integer between 1 and Sensitivity
  PotSetting = int(float(SENSITIVITY - 1) * float(PotValue - (POT_VALUE_LOW + 20))/float( (POT_VALUE_HIGH - 20) - (POT_VALUE_LOW + 20))) + 1;

  //Compute pulse Duration in milliseconds
  PulseDuration = PotSetting * TIMEUNIT;
//  Serial.println("Computing Pulse Duration in Milliseconds.");
//  Serial.println("Time Unit");
//  Serial.println(TIMEUNIT);
//  Serial.println("PotValue");
//  Serial.println(PotValue);
//  Serial.println("PotSetting");
//  Serial.println(PotSetting);
//  Serial.println("PulseDuration");
//  Serial.println(PulseDuration);
}

// function flashes the LED PotSetting number of times
void LEDBlinks() {
  int i=0;

  // Switch LED off for PAUSE_BEFORE_BLINK milliseconds prior to the blinks starting.
  digitalWrite(D_LEDPin, LOW);
  delay(PAUSE_BEFORE_BLINK);

  for (i = 0; i< PotSetting; i++) {
    digitalWrite(D_LEDPin, HIGH);
    delay(BLINK_ON_DURATION );
    digitalWrite(D_LEDPin, LOW);
    delay(BLINK_OFF_DURATION );
  }
}

// monitors the foot switch and counts the pulses
void MonitorFootSwitch() {
  unsigned long StartTime = 0; 
  int previousValue = 1;  //assume we get here with the first switch still down.
  int currentValue = 1;
  int changesDetected = 1;  // the very first pulse to get us here from the main loop.
  
  // get the start time
  StartTime = millis();

  while ( (abs(millis() - StartTime)) < MONITOR_FOOTSWITCH_PERIOD)
  {
    previousValue = currentValue;
    currentValue = digitalRead(D_FootButtonPin);
    if (previousValue != currentValue) {
      changesDetected = changesDetected + 1;
    }
  }

  if (currentValue==1) {
    changesDetected +=1; //assume that if it was high when we left the loop it will go low - means we always get an even number of changes.
  }
  numButtonClicks = floor((float)changesDetected/2.0);    
}

// continuously monitors the value on the Analog pin until PotValue is stable (i.e. no changes bigger than POT_NOISE)
// for STABILITY_TIME milliseconds.
void MonitorAnalog() {
  int PreviousPotValue = 0;
  int CurrentPotValue = 0;
  int KeepLooping = 1;
  unsigned long StartTime = 0; 
  unsigned long CurrentTime = 0; 

  // Set LED Pin high, so user knows that system has detected potentiometer change.
  digitalWrite(D_LEDPin, HIGH);

  // get the start time
  StartTime = millis();
  
  // start looping
  while (KeepLooping) {
    // Store the PotValue from the previous loop.
    PreviousPotValue = CurrentPotValue;

    // read in the new PotValue.
    CurrentPotValue = analogRead(A_PotPin);
    Serial.println(CurrentPotValue);
    // if the current PotValue has changed from the previous PotValue by more than POT_NOISE
    // then restart timer.
    if (abs(PreviousPotValue - CurrentPotValue)> POT_NOISE) {
      StartTime = millis();
    }

    // get the current time
    CurrentTime = millis();

    // Check for an overflow condition for the timer. The timer hits an overflow every fifty days.
    // If the system is left active for that long it is conceivable that the user adjusts the potentiometer
    // at precisely the moment the overflow occurs thus potentially getting locked into a 50 day wait.
    // If CurrentTime is lower than the StartTime then we must have hit the overflow condition.
    // Solution is simply to restart the timer. 
    // The user will just have to wait an additional STABILITY_TIME milliseconds for the stability condition to emerge.
    // Better than waiting an additional 50 days for the loop exit conditions to emerge.
    if (CurrentTime <= StartTime){
      StartTime = millis();
    }
   
    // if the time elapsed since the StartTime exceeds STABILITY_TIME then stop looping
    if ((CurrentTime - StartTime) > STABILITY_TIME) {
      KeepLooping = 0;
    }

    delay(MONITOR_DELAY); // put in delay to ensure that user has time to change the pot a significant amount between loops.
  }

  // switch off LED.
  digitalWrite(D_LEDPin, LOW);
}

void rapidFlash(int numPulses, int delayOn, int delayOff){
  int currentPulse = 0;
    for (currentPulse = 0; currentPulse < numPulses; currentPulse +=1) {
      digitalWrite(D_LEDPin, HIGH); // light the LED
      delay(delayOn); // wait for the pulse duration.
      digitalWrite(D_LEDPin, LOW);
      delay(delayOff); // wait for the pulse duration.
    }
}

void loop() {
  int pulsed = 0; // Set to zero at the beginning of each loop.
  int PotValueNew = 0; //initialise the new pot value
  int currentPulse = 0; // counter for number of pulses
  unsigned long startTime = 0; // timer

  digitalWrite(D_SolenoidPin, LOW);  //ensure output pins are set to low at the start of each loop.
  digitalWrite(D_LEDPin, LOW);

  // Read a new pot value.
  PotValueNew = analogRead(A_PotPin);
    
  // if the pot value has changed by more than POT_NOISE from the currently set value then
  // jump to a pot monitoring loop which exits when the pot is stable for STABILITY_TIME milliseconds.
  if (abs(PotValueNew - PotValue) > POT_NOISE)
  {
    MonitorAnalog(); // continuously reads the analog until it is stable for more than STABILITY_TIME;
    SetPulseDuration(); // Read the latest value and set the new pulse duration.
    LEDBlinks(); // blink the LED the appropriate number of times with the latest values.
  }

  // check for button presses
  numButtonClicks = 0; // assume no button clicks have happened/reset after last loop.
  numButtonClicks = digitalRead(D_FootButtonPin); // read the button pin.
  if (numButtonClicks == 1) {
    MonitorFootSwitch(); // as soon as button is pressed we monitor it for a some time to see if it is pressed repeatedly.
    // function sets the global variable numButtonClicks. 
  }

  //do behaviour based on global variable numButtonClicks. One is a single pulse
  if (numButtonClicks==1) {
        digitalWrite(D_SolenoidPin, HIGH);
        digitalWrite(D_LEDPin, HIGH); // light the LED
        delay(PulseDuration); // wait for the pulse duration.
        digitalWrite(D_SolenoidPin, LOW);  // close the solenoid and switch off the LED.
        digitalWrite(D_LEDPin, LOW);
  }

  // 2 clicks perform the pulse sequence.  Click to interrupt.
  if (numButtonClicks==2) 
  { 
    numButtonClicks = 0;
    delay(FOOTBUTTONDELAY);   
    for (currentPulse = 0; currentPulse < NUM_PROGRAMMED_PULSES; currentPulse +=1)
    {
      digitalWrite(D_SolenoidPin, HIGH);
      digitalWrite(D_LEDPin, HIGH); // light the LED
      delay(PROGRAMMED_SEQUENCE[currentPulse]); // wait for the pulse duration of the current time.
      digitalWrite(D_SolenoidPin, LOW);  // close the solenoid and switch off the LED.
      digitalWrite(D_LEDPin, LOW);
      
      startTime = millis();
      while ((numButtonClicks == 0)&&((millis() - startTime) <PROGRAMMED_PULSE_DELAY)) 
      {
        numButtonClicks = digitalRead(D_FootButtonPin);
      }
  
      if (numButtonClicks>0) 
      {
         rapidFlash(5,100,100);
         break;         
      }
    }
    numButtonClicks = 0;
    delay(FOOTBUTTONDELAY);
  }
 
  if (numButtonClicks >2){ // an error alert
     rapidFlash(5, 100, 100);
     delay(FOOTBUTTONDELAY);
  }
}

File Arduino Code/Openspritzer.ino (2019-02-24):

/* 
 
        OpenSpritzer v1.3, an open hardware pressure ejection system.

This Arduino file is designed to be uploaded on an Arduino Nano for the OpenSpritzer project 
Source : https://github.com/BadenLab/Openspritzer
This project is Open Source licensed, released under CERN OHL v1.2

by  C.J. Forman & M.J.Y. Zimmermann, 2019.02.05
Baden Lab, CRPC, School of Life Sciences, University of Sussex, United Kingdom

                                                                                              */

////////////////////////////////////////////////////////////////////////////////////////////////
//                         KEY PARAMETERS TO SET BY USERS
////////////////////////////////////////////////////////////////////////////////////////////////

  const int POT_LOW           = 0;      // Lowest value read from the potentiometer.
  const int POT_HIGH          = 1023;   // Highest value read from the potentiometer 
  const int PotNoise          = 10;     // Error value added to the potentiometer reading (0 - 1023)
  
  const int PULSE_LOW         = 10;     // Minimum Pulse Duration in ms
  const int PULSE_HIGH        = 1000;   // Maximum Pulse Duration in ms
  
  const int PULSE_Delay       = 500;    // Minimum time between two sucessive button push in ms

  
////////////////////////////////////////////////////////////////////////////////////////////////
//                               GLOBAL VARIABLES
//////////////////////////////////////////////////////////////////////////////////////////////// 
  
  // Set up the pins
  const int FootPin           = 2;      // Set the foot pedal to digital pin 2
  const int SolenoidPin       = 5;      // Set the solenoid valve to digital pin 5
  const int LEDPin            = 10;     // Set proxy LED to digital pin 10
  const int PotPin            = A0;     // Set the potentiometer to analog pin A0
  

  // Declare global variables
 
  int PotValue                = 0;      // Potentiometer value reading
  int CurrentPotValue         = 0;      // Current potentiometer value read

  int Pulse_Duration          = 0;      // Amount of time the pulse is on
  word BaudRate               = 9600;   // Baud Rate



////////////////////////////////////////////////////////////////////////////////////////////////   
//                                        MODULES
//////////////////////////////////////////////////////////////////////////////////////////////// 

void SetPulseDuration() {               
  // Read the potentiometer value and define the pulse duration accordingly
  PotValue = analogRead(PotPin);
  Pulse_Duration = map(PotValue,POT_LOW,POT_HIGH,PULSE_LOW,PULSE_HIGH);
  }

void LED(){                             
    // The proxy LED blinks as long as the last set pulse duration
    PotValue = analogRead(PotPin);
    Pulse_Duration = map(PotValue,POT_LOW,POT_HIGH,PULSE_LOW,PULSE_HIGH);
    digitalWrite(LEDPin,HIGH);
    delay(Pulse_Duration);
    digitalWrite(LEDPin,LOW);
}

void Pulse(){   
  // Open the Valve, Blink the LED for the define Pulse Duration time                        
  digitalWrite(SolenoidPin, HIGH);
  digitalWrite(LEDPin, HIGH); // light the LED
  delay(Pulse_Duration); // wait for the pulse duration.
  digitalWrite(SolenoidPin, LOW);  // close the solenoid and switch off the LED.
  digitalWrite(LEDPin, LOW);
}



////////////////////////////////////////////////////////////////////////////////////////////////   
//            SETUP (this only runs once at when the Arduino is initialised)
//////////////////////////////////////////////////////////////////////////////////////////////// 

void setup() {
  // Initialise the serial communication with PC
  Serial.begin(BaudRate);
  
  // Initialize the pins
  pinMode(PotPin, INPUT);
  pinMode(FootPin, INPUT);
  pinMode(LEDPin, OUTPUT);
  pinMode(SolenoidPin, OUTPUT);

  // Set initial conditions on pins. Prevent pulse from happening
  digitalWrite(SolenoidPin, LOW);
  digitalWrite(LEDPin, LOW);

  // Set the first pot value and the first pulse duration
  SetPulseDuration();
}


////////////////////////////////////////////////////////////////////////////////////////////////
//                                      MAIN LOOP
////////////////////////////////////////////////////////////////////////////////////////////////
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

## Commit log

2018-07-26 created PCB, missing outline and screw pads
    [OpenSpritzer.kicad_pcb, OpenSpritzer.sch]
2018-07-27 update board. Main is done
    [OpenSpritzer-B.Cu.gbr, OpenSpritzer-B.Mask.gbr, OpenSpritzer-B.Paste.gbr, OpenSpritzer-B.SilkS.gbr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]
2018-07-27 board with hardware licence and links
    [OpenSpritzer-B.Cu.gbr, OpenSpritzer-B.Mask.gbr, OpenSpritzer-B.Paste.gbr, OpenSpritzer-B.SilkS.gbr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]
2018-08-07 pcb addon
    [OpenSpritzer-B.Adhes.gbr, OpenSpritzer-B.CrtYd.gbr, OpenSpritzer-B.Cu.gbr, OpenSpritzer-B.Fab.gbr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]
2018-08-07 PCB Board
2018-09-07 Version 1.01
    [BOM.csv, OpenSpritzer-B.Adhes.gbr, OpenSpritzer-B.CrtYd.gbr, OpenSpritzer-B.Cu.gbr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]
2018-09-09 version 1.02
    [OpenSpritzer-B.Cu.gbr, OpenSpritzer-B.Mask.gbr, OpenSpritzer-Cmts.User.gbr, OpenSpritzer-F.CrtYd.gbr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]
2018-10-02 V 1.02
    [OpenSpritzer_1.02.sch]
2018-10-08 Update Manuscript and Instruction/BOM.csv
    [BOM.csv]
2018-10-08 v 1.2
    [BOM.csv, OpenSpritzer.scad]
2018-10-11 Bill of Materials
    [BOM.csv]
2018-10-11 Arduino Code
2018-12-12 v 1.3
    [OpenSpritzer v1.3.scad, Right.stl]
2020-03-08 Update OpenSpritzer v1.3.scad
    [OpenSpritzer v1.3.scad]
2020-08-03 rename gerber to gerbers and start working on 1-click-bom.tsv
    [1-click-bom.tsv, OpenSpritzer_1.3-B.Adhes.gbr, OpenSpritzer_1.3-B.CrtYd.gbr, OpenSpritzer_1.3-B.Cu.gbr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]
2020-08-06 update boms
    [1-click-bom.tsv, BOM.csv]
2020-08-08 update 1-click-bom
    [1-click-bom.tsv]
